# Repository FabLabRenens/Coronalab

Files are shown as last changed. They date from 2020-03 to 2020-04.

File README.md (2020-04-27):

# Coronalab

**Dépot de différents projets réalisés durant la pandémie du covid19.**

## Lunettes de protection | _Protective glasses_

Lunettes de protection utilisées en milieu hospitalier. Modèle réalisé à la demande des hôpitaux universitaires afin d'assurer la continuité de l'approvisionnement avec l'aide des fablab, makerspace et tiers-lieux en mesure de contribuer.

Le modèle est composé d'une **monture** à imprimer en 3D (FDM) ainsi que d'une **visière** découpée dans un film en polyester d'une épaisseur comprise entre 0.130 et 0.200 mm.

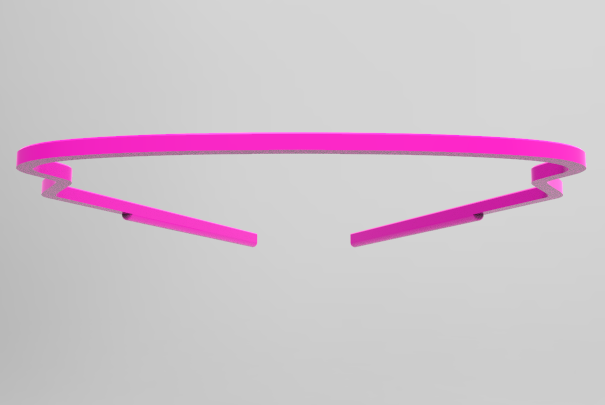
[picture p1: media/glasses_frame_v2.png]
*+*
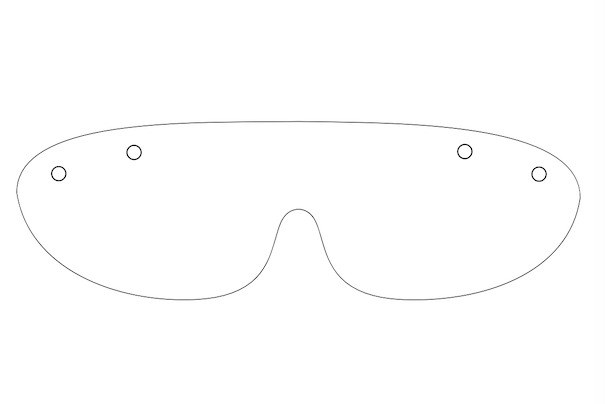
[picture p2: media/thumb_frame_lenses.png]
*=*
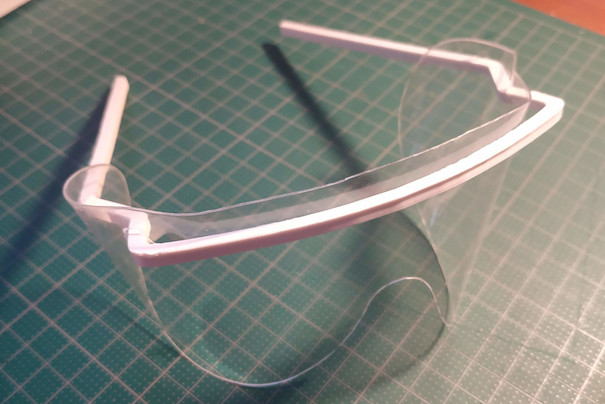
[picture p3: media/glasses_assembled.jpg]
prototype imprimé et découpé par Matthieu Borgognon


Après une phase initiale de récolte d'informations, de prototypage et de test (lire [l'historique des points de situation](https://github.com/FabLabRenens/Coronalab/wiki/Historique)), il est temps de passer à la **production**.

## Pourquoi ce projet ?

Ces lunettes répondent à une demande précise et donc à un besoin avéré des responsables du CHUV (Lausanne-Vaud) et des HUG (Genève), qui sont confrontés à la menace d'une pénurie puisque en ce moment l'approvisionnement par les canaux habituels est fortement perturbé voire impossible.
Elles sont utilisées par presque tous les services, au delà de ceux qui sont directement confrontés aux cas avérés de COVID-19. La situation actuelle menace d'aboutir à une pénurie qui affecterait l'ensemble des services.

Cet [article sur le site du fablab Renens](http://www.fablab-renens.ch/news/covid19-que-faisons-nous/) illustre le chemin qui nous a amené jusqu'ici.

## En quoi consiste notre engagement ?

Les besoins évoluent sans cesse, mais actuellement ils sont chiffrés à 700 montures et 4500 visières **par semaine**.

### A propos de licence

Il n'est pas dans l'éthique des FabLabs de copier des marchandises.  
Il n'est pas dans l'éthique des FabLabs de priver le personnel médical d'un outil précieux alors qu'ils peuvent se donner les moyens de le produire.  
Nous fournissons ici les modèles pour permettre aux FabLabs, Makerspace, Tiers-Lieux et à toutes les personnes en mesure de le faire de contribuer à produire ces objets dont il y a actuellemment pénurie. Nous faisons ça à la demande des institutions de santé et dans le seul et unique but de soutenir le personnel soignant avec cet équipement de sécurité. Ces modèles seront retirés de ce site dès que l'approvisionnement de la part des hôpitaux sera de noveau possible par les canaux commerciaux habituels. Nous ne pouvons attribuer aucune licence à ces modèles, ni offrir aucune garantie légale pour leur production et leur utilisation. Il incombe à chaque personne qui télécharge ces modèles de s'assurer de la conformité juridique de son action. Si vous voulez fabriquer ces objets à la demande d'une institution de santé, nous vous conseillons de discuter préalablement avec celle-ci des aspects légaux sous-jacents pour que vous soyez protégé.

### Visières
Pour la découpe des **visières** nous essayons en priorité d'avoir recours à de l'**équipement industriel** (découpeuses à lames), capable de produire plus aisément dans les volumes requis. En fonction de l'évolution des besoins, difficile à anticiper, une mise à contribution des découpeuses laser de nos labs et spaces pourrait être envisageable. Les fichiers pour la découpe (découpeuse à lames ou laser) sont disponibles en [svg](glasses/glasses_lenses.svg) et [dxf](glasses/glasses_lenses.dxf) (unité: mm).  
Pour une découpe manuelle de petites séries, Jochen Hanselmann a créé un [guide / emporte-pièce à imprimer en 3d](glasses/glasses_template-3.stl), avec une [image qui en illustre le principe de fonctionnement](glasses/template_jh_howto.jpeg). *Attention*: les trous doivent être réalisés avec un perforateur à feuilles, ou avoir un diamètre suffisant.

### Impression en 3D des **montures**

Le modèle est ici: [glasses_frame_v2.stl](glasses/glasses_frame_v2.stl) (unité: mm).
__Mise à jour du 16 avril 2020__: une nouvelle version est désormais en ligne. Il s'agit d'une autre variante de lunettes utilisées couramment qui présente l'avantage d'être plus large et de mieux accomoder les visières.  
Si vous imprimez des montures en ce moment, __merci d'utiliser ce nouveau modèle pour tout nouveau sachet de 10__ (finissez d'abord les impressions nécessaires pour remplir le sachet de 10, merci de ne pas mélanger les deux modèles dans le même sachet!  
La nouvelle version des montures est légèrement plus large à certains endroits (d'environ 5 mm). Par conséquent, il n'est plus possible sur certaines imprimantes d'imprimer 3 montures en même temps.

Nous l'avons testé en PETG et PLA. Le modèle en PETG a été validé par le CHUV, celui en PLA pas encore.
En principe l'ABS doit aussi être possible.
Sur la plupart des machines FDM les plus courantes il est possible d'arranger plusieurs (au moins 2) montures par batch d'impression.

Il y a aussi des [fichiers avec profiles prêts à l'emploi](https://github.com/FabLabRenens/Coronalab/wiki/Print-profiles). La liste est destinée à s'étouffer. Si vous imprimez avec succès en utilisant une configuration matériel/machine qui ne figure pas encore dans la liste, merci de nous l'envoyer à fablab_renens_su@googlegroups.com pour que tout le monde puisse en profiter.

Lors de l'impression, attention à l'effet "patte d'elephant" (cf. par exemple [cette description du problème](https://support.3dverkstan.se/article/23-a-visual-ultimaker-troubleshooting-guide#elephant)). Il existe une [variante du modèle stl](glasses/glasses_frame_bigger_chamfer_v2.stl) avec un chamfrin plus important pour tenter de mitiger ce problème, mais les test ne sont pas encore conclus). Les slicer courants offrent aussi des réglages (souvent appelés "elephant foot compensation ou "Initial Layer Line Width") pour mitiger cet effet .
Au final, *vérifiez que le bord inférieur des montures* 1) ne soit pas coupant ou désagréable au contact 2) puisse entrer dans les trous correspondants sur les visières (cercles de 6 mm de diamètre).

Les fichiers suivants sont également disponibles:

- code source du dessin, Alibre Design ou Atom3D: [glasses_frame_v2.AD_PRT](glasses/glasses_frame_v2.AD_PRT), et dessin 2D y relatif [glasses_frame_v2.AD_DRW](glasses/glasses_frame_v2.AD_DRW).

- profil 2D: [dxf 14](glasses/glasses_frame_v2.dxf) et [pdf](glasses/glasses_frame_v2.pdf).
- dessin au format STEP AP 214: [glasses_frame_v2_step_ap_214.stp](glasses/glasses_frame_v2_step_ap_214.stp)

| 👉 | Pour toute question contactez-nous:  fablab_renens_su@googlegroups.com |
|----| :-------:|

## Visières faciales intégrales

Nous pensions découper la visiere conçue par Konrad Klepacki et Mateusz Dyrda.
https://hackaday.io/project/170481-laser-cut-medical-shield
Cette visière présente l'avantage d'être produite uniquement par découpage de feuilles de PETG de 0.5 mm d'épaisseur.

- Nous ne l'avons pas testée : les fichiers sont dans le répertoire VF

Nous pouvons utiliser le même film de 130 ou 180 microns employé pour les lunettes avec ce modéle de structure :
https://www.myminifactory.com/fr/object/3d-print-115247?fbclid=IwAR2c9N3aFWIlBcmv_PWLbtqA287igzUk3-ZPRXvf5xEHGqIFypm60IjLfNA

- [newshieldsupport-org-notext.stl](ns/newshieldsupport-org-notext.stl)

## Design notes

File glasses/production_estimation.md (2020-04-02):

# Production estimation 

The weekly output is estimated with 10h per 7 days, with two 5h shifts per day.
Assuming a 70% efficiency (total guess)

Output: 70h * items per hour * 0.7

## 28-03-2020 
Based on rough estimates, not with final materials.

### 3d Printing
#### One frame per plate, matthieu's setup
22 min (without cooldown)
Esimated 5 minute cooldown and cleanup

#### One frame per plate, juuso's setup
38 min
3 min cooldown

#### Three frames per plate, juuso's setup
105 minutes
3 min cooldown

#### Three frames per plate, matthieu's setup (estimate)
61 minutes (105 * 22 / 38)
3 min cooldown

### Laser cut
20 s (without cooldown) per piece
Estimate 1 minute for cooldown and changing plate

### Output per week
Single frame in a print: 108 frames per week per printer
Three frames in a print: 137 frames per week per printer (and less manual time)

2205 visors per week per laser cutter

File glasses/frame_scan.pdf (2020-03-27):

I^

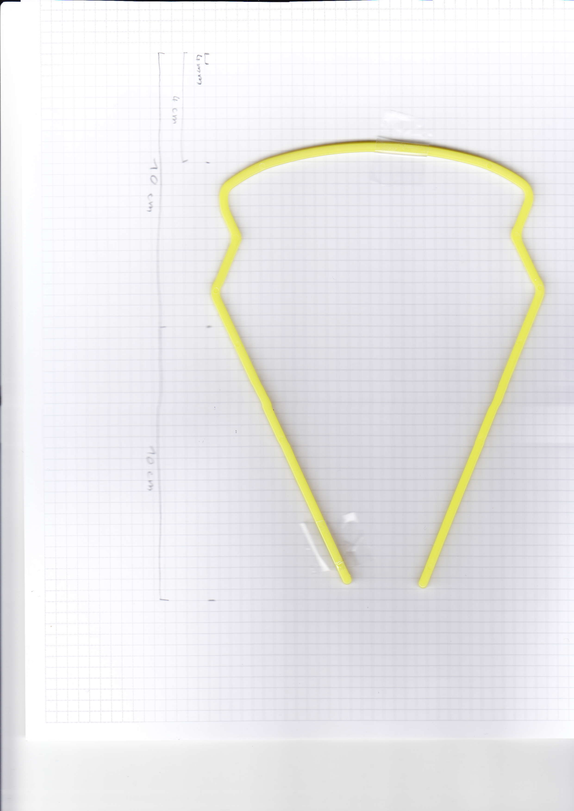
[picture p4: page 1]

: | ..
3
It

\
,t\

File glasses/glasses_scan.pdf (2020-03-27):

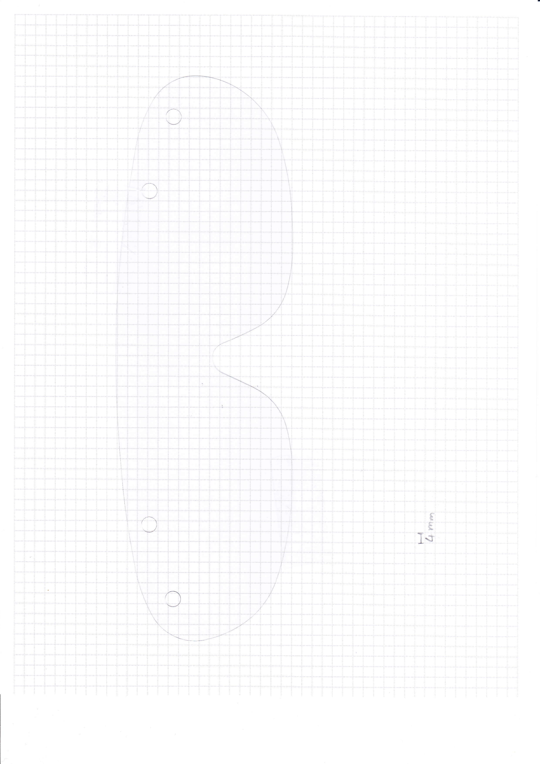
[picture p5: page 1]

t-)

---/

'.:-,
\
\
\

ì-
"l-'S
o

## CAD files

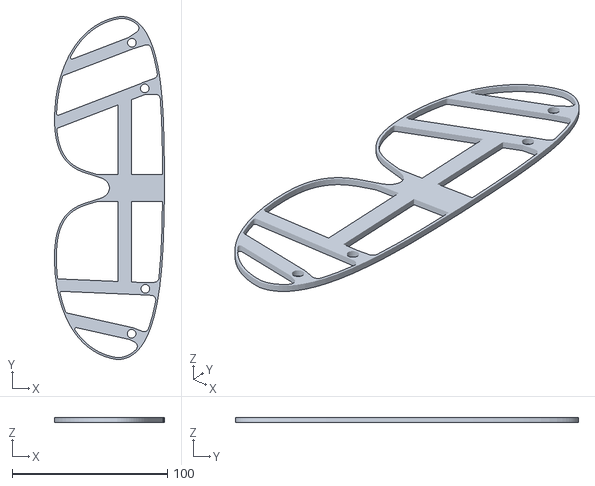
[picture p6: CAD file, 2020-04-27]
glasses/glasses_template-3.stl
70.8 x 220.9 x 3.00

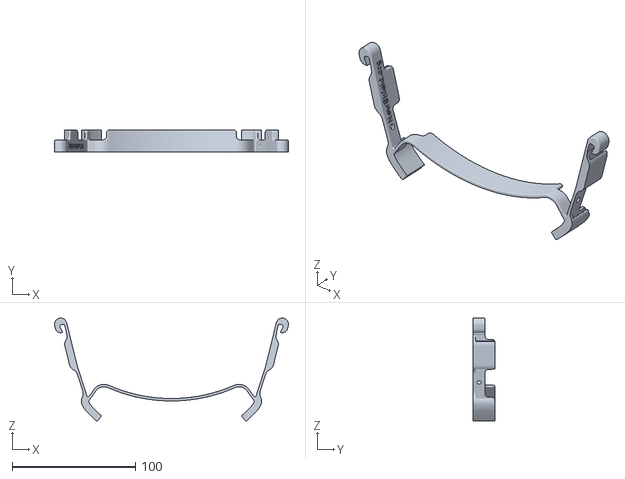
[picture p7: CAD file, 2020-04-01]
ns/newshieldsupport-org-notext.stl
190.2 x 18.0 x 83.7

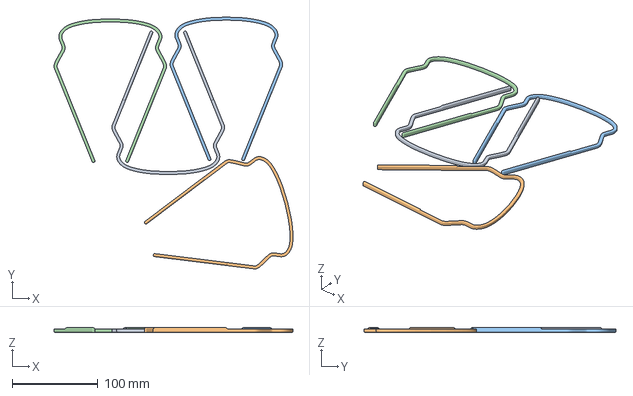
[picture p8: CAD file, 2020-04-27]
print-profiles/CCR10_glasses_frame_bigger_chamfer_v2_4modeles.3mf
278.1 x 293.1 x 5.25 mm

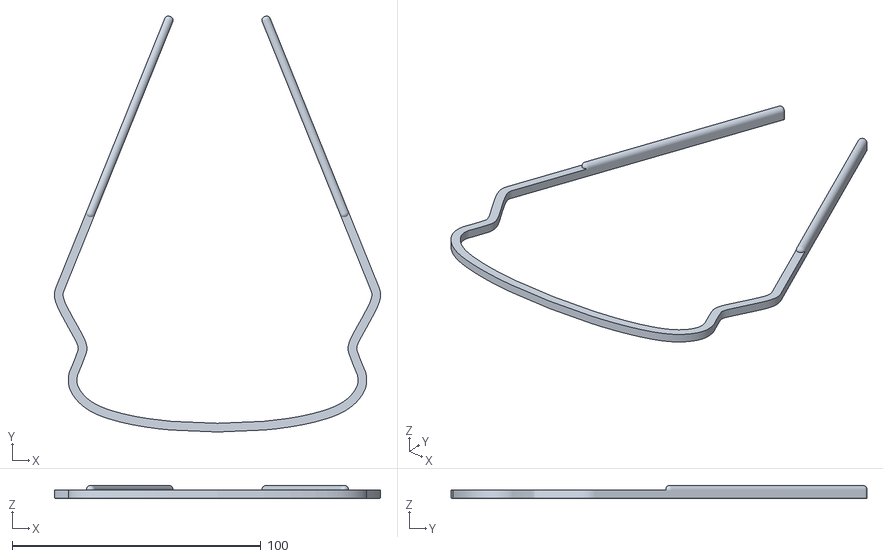
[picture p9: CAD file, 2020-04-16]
glasses/glasses_frame_v2.stl
131.1 x 167.2 x 5.25

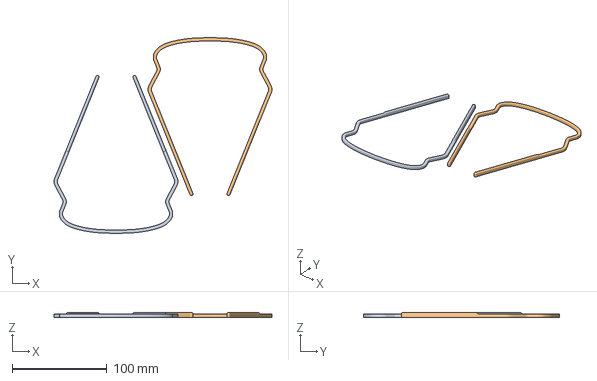
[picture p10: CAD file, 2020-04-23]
print-profiles/Prusa-2x-glasses_frame_v2_0.6_PETG_Extrudr.3mf
230.5 x 207.3 x 5.25 mm
glasses_frame_v2.stl x 2

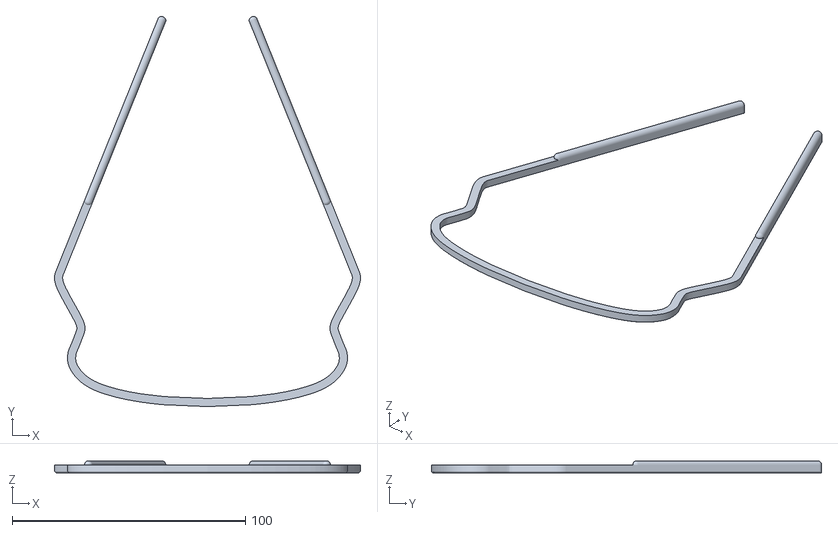
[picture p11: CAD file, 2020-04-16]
glasses/glasses_frame_bigger_chamfer_v2.stl
131.1 x 167.2 x 5.25

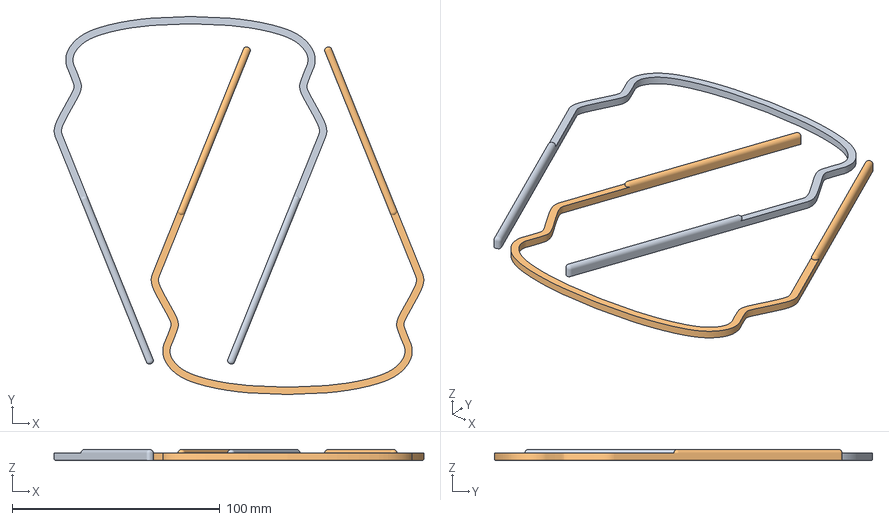
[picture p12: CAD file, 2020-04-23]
print-profiles/UM3_2x_glasses_frame_v2_extruder_PETG_0_4.3mf
177.8 x 181.8 x 5.25 mm

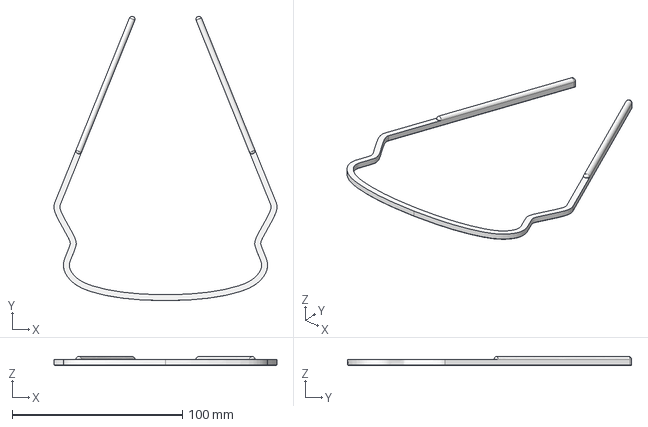
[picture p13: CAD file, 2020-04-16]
glasses/glasses_frame_v2_step_ap_214.stp
131.1 x 167.2 x 5.25 mm

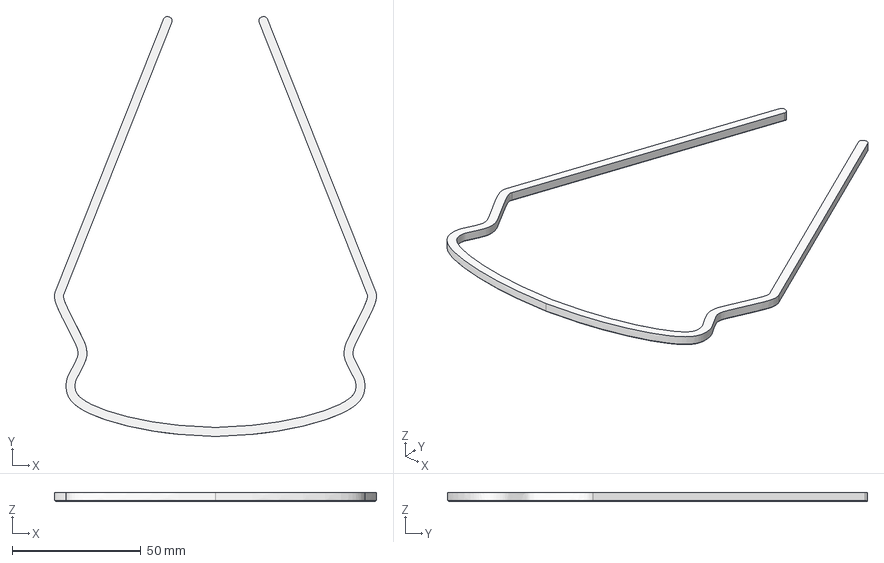
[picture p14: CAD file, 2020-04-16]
glasses/glasses_frame_bare_step_ap_214.stp
125.1 x 163.2 x 3.50 mm

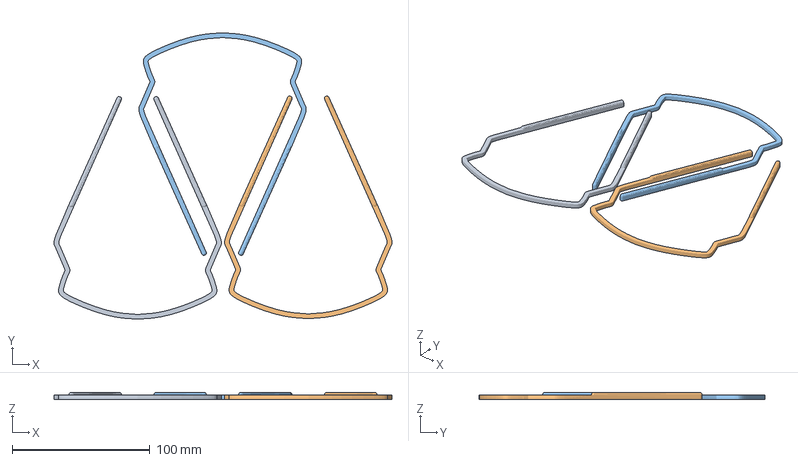
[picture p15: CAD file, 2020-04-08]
print-profiles/Prusa-3x-glasses_frame_0.6_PETG_Extrudr.3mf
245.4 x 207.9 x 5.23 mm
glasses_frame.stl x 2

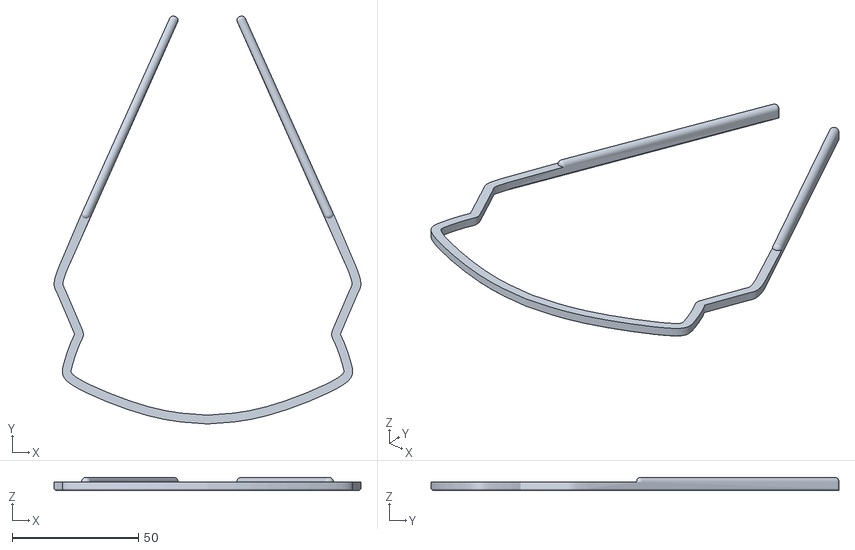
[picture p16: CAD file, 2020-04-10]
glasses/glasses_frame_bigger_chamfer.stl
121.6 x 161.6 x 5.25

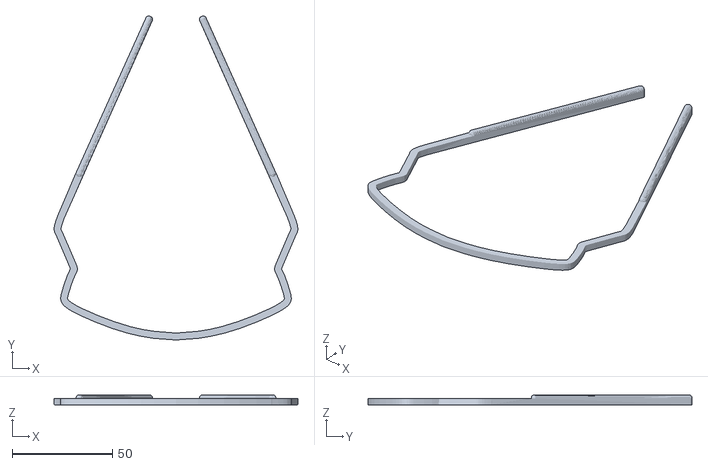
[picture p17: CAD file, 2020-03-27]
glasses/glasses_frame.stl
121.5 x 161.6 x 5.23

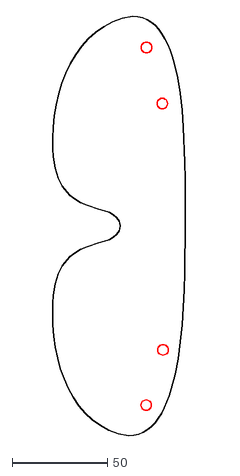
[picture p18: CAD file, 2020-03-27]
glasses/glasses_lenses.dxf
73.3 x 219.7

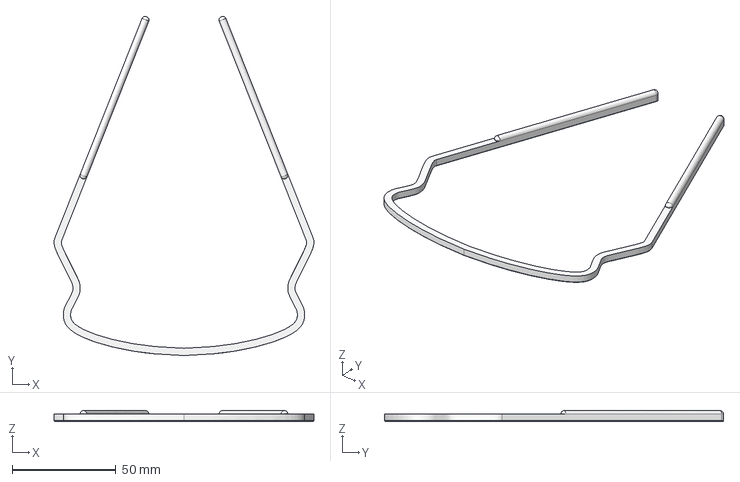
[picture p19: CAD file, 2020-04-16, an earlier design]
glasses/previous_versions/glasses_frame_v1_1_step_ap_214.stp
125.1 x 163.2 x 5.25 mm

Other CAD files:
print-profiles/Prusa-2x-glasses_frame_v2_0.4_PETG_Extrudr.3mf
print-profiles/TEST_NOT_VALIDATED_Prusa-3x-glasses_frame_0.6_PLA_Dutch_Filament.3mf
print-profiles/Prusa-3x-glasses_frame_0.4_PETG_Extrudr.3mf
glasses/previous_versions/glasses_frame_v1_1.stl
glasses/glasses_frame.dxf
glasses/glasses_frame_v2.dxf

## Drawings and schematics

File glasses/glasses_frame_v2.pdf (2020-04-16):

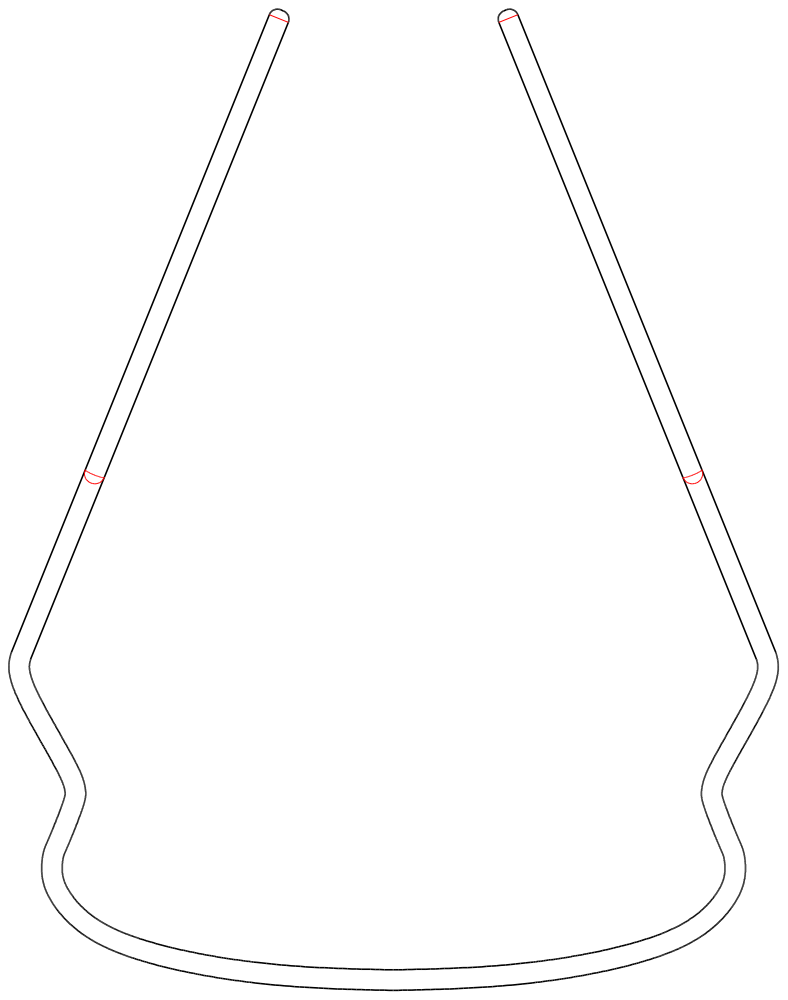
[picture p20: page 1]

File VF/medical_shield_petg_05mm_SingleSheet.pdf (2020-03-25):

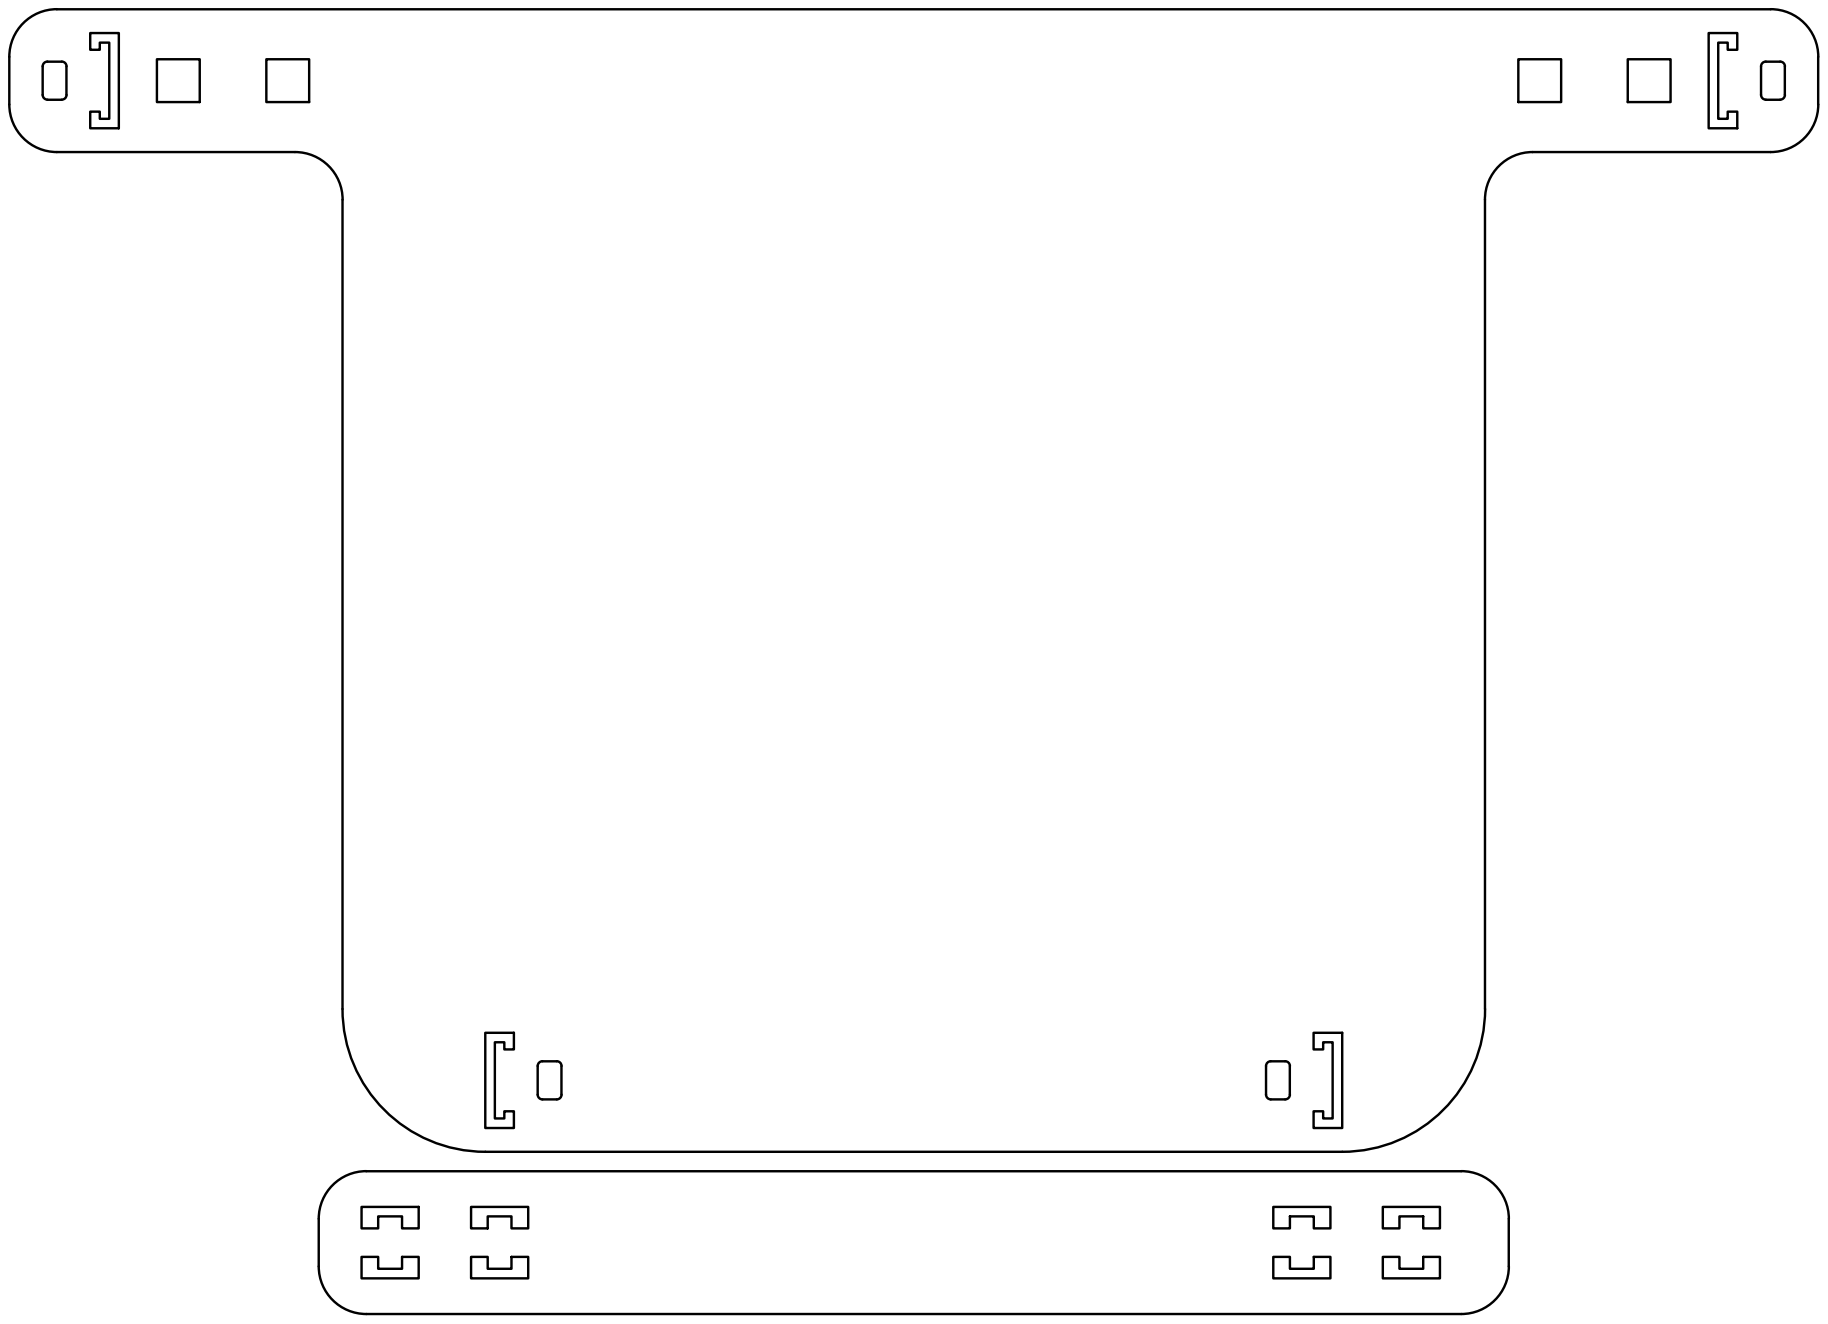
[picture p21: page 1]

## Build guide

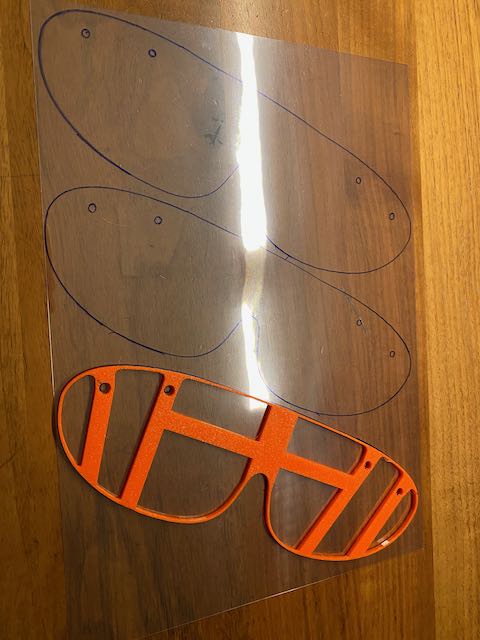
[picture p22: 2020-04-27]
glasses/template_jh_howto.jpeg

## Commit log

2020-03-25 Angles arrondis monture
    [safeview.dxf]
2020-03-25 Modification monture
    [monture.scad, monture.stl]
2020-03-27 Modification masque
    [safeview.dxf]
2020-03-27 Added new frame prototype, updated readme
    [glasses_frame.stl]
2020-03-27 Added rendering of frame
2020-03-27 monture rt provisoire
    [monture_3.stl]
2020-03-27 Updated readme and structure
    [glasses_frame_test.stl, glasses_lenses.dxf]
2020-03-27 Fixed glasses frame 3d mesh with 3D Builder
    [glasses_frame.stl]
2020-03-27 First glasses assembly
2020-03-27 Rotate assembly image with it's exif orientation metadata and resize
2020-03-27 Upload new rotated and resize assembly file
2020-03-27 Ajust assembly img size
2020-03-27 Update resizing assembly img
2020-03-27 Final size assembly img
2020-03-28 Ajout données centrale d'achat CHUV/HUG + lien temps de fabrication
2020-03-28 Update production_estimation.md
    Refined estimates based on test run with multiple frames per print.
2020-03-29 Ajout vf test
    [vf_frame.stl, vf_lenses.dxf]
2020-03-30 Added STEP export of the frame
    [glasses_frame_step_ap_242.stp]
2020-03-30 Added 2D export of the frame, updated readme accordingly
    [glasses_frame.dxf]
2020-04-01 Ajout shield
    [newshieldsupport-org-notext.stl]
2020-04-01 Point de situation avec centrale d'achat HUG/CHUV
2020-04-04 Upload first print profile by Nicolas Martin Clément
    [3x-glasses_frame-extrudr_petg-prusa_i3mk3s-by-nmc.3mf]
2020-04-04 Substantial refactoring of the readme, made more readable.
    [glasses_frame.dxf, glasses_frame.stl, glasses_frame_step_ap_242.stp, glasses_frame_test.stl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]
2020-04-08 new profiles by Nicolas
    [Prusa-3x-glasses_frame_0.4_PETG_Extrudr.3mf, Prusa-3x-glasses_frame_0.6_PETG_Extrudr.3mf, Prusa-3x-glasses_frame_0.6_PLA_Dutch_Filament.3mf]
2020-04-08 Removed redundant print profile
    [3x-glasses_frame-extrudr_petg-prusa_i3mk3s-by-nmc.3mf]
2020-04-08 renaming unvalidated profile to avoid confusion
    [TEST_NOT_VALIDATED_Prusa-3x-glasses_frame_0.6_PLA_Dutch_Filament.3mf]
2020-04-10 Added variant with bigger chamfer, added some printing instructions
    [glasses_frame_bigger_chamfer.stl]
2020-04-10 removed openscad trial to avoid confusion
    [glasses_frame_test.stl]
2020-04-16 Update frame rendering to new version
2020-04-16 Uploaded v2 of the frame, modified readme, cleaned up older files
    [glasses_frame.stl, glasses_frame_bare_step_ap_214.stp, glasses_frame_bigger_chamfer.stl, glasses_frame_bigger_chamfer_v2.stl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]
2020-04-23 update print profiles with v2
    [Prusa-2x-glasses_frame_v2_0.4_PETG_Extrudr.3mf, Prusa-2x-glasses_frame_v2_0.6_PETG_Extrudr.3mf, UM3_2x_glasses_frame_v2_extruder_PETG_0_4.3mf]
2020-04-27 Add creality CR10 profiles by Kilian Borgeaud
    [CCR10_glasses_frame_bigger_chamfer_v2_4modeles.3mf]
2020-04-27 Added template by Jochen Anselmann
    [glasses_template-3.stl]
